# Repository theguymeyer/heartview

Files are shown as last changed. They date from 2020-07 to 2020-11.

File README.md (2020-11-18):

# Welcome to HeartView

A real-time testing system for pacemaker prototypes. 

The pacemaker project is a long standing challenge by Boston Scientific sponsored by McMaster University's Center for Software Certification -> [More](http://sqrl.mcmaster.ca/pacemaker.htm). This repo is the open-source (GPLv3) code base for the HeartView Testing GUI, embedded development files, and design files for the hardware and electrical systems. Even more info [here](https://guymeyer.me/project/heartview).

## Directory

HeartView Documentation -> https://github.com/theguymeyer/heartview/blob/master/course_dev/documentation/heartview_explained/intro_to_heartview.pdf

MacOS Executeable for HeartView -> https://github.com/theguymeyer/heartview/tree/master/course_dev/ui-HeartView/mac/exe

Windows Executeable for HeartView -> https://github.com/theguymeyer/heartview/tree/master/course_dev/ui-HeartView/win/exe

Nucleo Embedded Codebase -> https://github.com/theguymeyer/heartview/tree/master/course_dev/shield_nucleo_rev0/CubeMX

PCB Build Packages -> https://github.com/theguymeyer/heartview/tree/master/course_dev/Production/build

Heart Shield Design (Nucleo) -> https://github.com/theguymeyer/heartview/tree/master/course_dev/shield_nucleo_rev0

Pacemaker Shield Design -> https://github.com/theguymeyer/heartview/tree/master/course_dev/shield_pacemaker

Mechanical Design (casing) -> https://github.com/theguymeyer/heartview/tree/master/course_dev/casing/rev0

Testing Files -> https://github.com/theguymeyer/heartview/tree/master/course_dev/testing

## How to get involved

We invite you to contribute and help build a robust way to learn about pacemakers in a fun and engaging way. Reach out to the McSCert Research Group at McMaster Univeristy or get in touch view GitHub.

image of the heartview testing system The HeartView System

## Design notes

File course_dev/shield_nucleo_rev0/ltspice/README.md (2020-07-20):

# Documentation for the testing controller shield

The model is developed using LTspice with imported models. No model was found for the TLE2426CDR Rail Splitter chip so the model does not currently compile

The most up-to-date model is titled "nucleo_shield_heart_interface_rev2.asc"

### Notes on In Amp circuitry

- This Circuit was designed from information in this document (p.5-3 was especially helpful) (https://www.analog.com/media/en/training-seminars/design-handbooks/designers-guide-instrument-amps-complete.pdf)
- Desired Gain: 1/2
- Vcm = GND // the middle of the expected input dynamic range 
- note... the in-amp’s input buffers will need to swing both positive and negative with respect to ground
- Vref = 2.5V //  centered on the expected output dynamic range
- "A good guideline is to keep IBR < 10 mV" (p.5-3)
- Need to use "1% metal film resistors"

### Notes on pulse generation circuitry

Pulse Characteristics:
 - 5V square pulse
 - duration ranges from 100 us to 5 ms (according to PACEMAKER doc)

**IMPORTANT** The onboard toggle switch found on the pacemaker shield MUST be placed to 'x100' in order to comply with the pulse characteristics
 
Note: Recent discoveries in pacemaker shield show that the 
pulse is substantially filtered when nearing 3ms PW or below

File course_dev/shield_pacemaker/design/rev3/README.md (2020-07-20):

# Pacemaker Shield - Revision 3

Use this folder to store files related to the current revision developed by CG Tech Inc (Company Contact: Gil Elgez)

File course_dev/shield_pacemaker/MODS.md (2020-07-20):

# Shield Modifications

This document specifies the alterations needed for the Pacemaker shield (shield A). The current design of the shield can be found under,
        >> design >> rev2

## Mod 1 - Pin Swaps

The current revision (rev2) of the shield contains incorrect pin routing on certain pins. The corrections are outlined in "pin_swap_mod.png"

## Mod 2 - Replacing Connector X1

The goal is to provide a solution that will be allow for easy connections of jumper wires.
Note that each pin is connected twice to the board, a single PCB connection is **assumed** to suffice.

Instructions:
- update the BOM to include female header pins 
- ensure that the PCB matches the updated pins

## Mod 3 - Replacing Connector SV1

The current pins are incompatible with standard jumper wires. As such this part is to be changed in BOM to include 0.1" male header pins that fit female jumper wires connectors.

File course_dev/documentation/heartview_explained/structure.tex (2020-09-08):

%%%%%%%%%%%%%%%%%%%%%%%%%%%%%%%%%%%%%%%%%
% The Legrand Orange Book
% Structural Definitions File
% Version 2.1 (26/09/2018)
%
% Original author:
% Mathias Legrand (legrand.mathias@gmail.com) with modifications by:
% Vel (vel@latextemplates.com)
% 
% This file was downloaded from:
% http://www.LaTeXTemplates.com
%
% License:
% CC BY-NC-SA 3.0 (http://creativecommons.org/licenses/by-nc-sa/3.0/)
%
%%%%%%%%%%%%%%%%%%%%%%%%%%%%%%%%%%%%%%%%%

%----------------------------------------------------------------------------------------
%	VARIOUS REQUIRED PACKAGES AND CONFIGURATIONS
%----------------------------------------------------------------------------------------

\usepackage{graphicx} % Required for including pictures
\graphicspath{{res/}} % Specifies the directory where pictures are stored

\usepackage{lipsum} % Inserts dummy text

\usepackage{tikz} % Required for drawing custom shapes

\usepackage[english]{babel} % English language/hyphenation

\usepackage{enumitem} % Customize lists
\setlist{nolistsep} % Reduce spacing between bullet points and numbered lists

\usepackage{booktabs} % Required for nicer horizontal rules in tables

\usepackage{xcolor} % Required for specifying colors by name
\definecolor{ocre}{RGB}{243,102,25} % Define the orange color used for highlighting throughout the book

%----------------------------------------------------------------------------------------
%	MARGINS
%----------------------------------------------------------------------------------------

\usepackage{geometry} % Required for adjusting page dimensions and margins

\geometry{
	paper=a4paper, % Paper size, change to letterpaper for US letter size
	top=3cm, % Top margin
	bottom=3cm, % Bottom margin
	left=3cm, % Left margin
	right=3cm, % Right margin
	headheight=14pt, % Header height
	footskip=1.4cm, % Space from the bottom margin to the baseline of the footer
	headsep=10pt, % Space from the top margin to the baseline of the header
	%showframe, % Uncomment to show how the type block is set on the page
}

%----------------------------------------------------------------------------------------
%	FONTS
%----------------------------------------------------------------------------------------

\usepackage{avant} % Use the Avantgarde font for headings
%\usepackage{times} % Use the Times font for headings
\usepackage{mathptmx} % Use the Adobe Times Roman as the default text font together with math symbols from the Sym­bol, Chancery and Com­puter Modern fonts

\usepackage{microtype} % Slightly tweak font spacing for aesthetics
\usepackage[utf8]{inputenc} % Required for including letters with accents
\usepackage[T1]{fontenc} % Use 8-bit encoding that has 256 glyphs

%----------------------------------------------------------------------------------------
%	BIBLIOGRAPHY AND INDEX
%----------------------------------------------------------------------------------------

% original source code - broken for my installtion
%\usepackage[style=numeric,citestyle=numeric,sorting=nyt,sortcites=true,autopunct=true,babel=hyphen,hyperref=true,abbreviate=false,backref=true,backend=biber]{biblatex}
%\addbibresource{bibliography.bib} % BibTeX bibliography file
%\defbibheading{bibempty}{}

\usepackage[style=numeric, sorting=none, backend=bibtex, backref, doi=false]{biblatex}	% Use Biblatex for customization of bib
\addbibresource{./bibliography.bib} % BibTeX bibliography file

\usepackage{calc} % For simpler calculation - used for spacing the index letter headings correctly
\usepackage{makeidx} % Required to make an index
\makeindex % Tells LaTeX to create the files required for indexing

%----------------------------------------------------------------------------------------
%	MAIN TABLE OF CONTENTS
%----------------------------------------------------------------------------------------

\usepackage{titletoc} % Required for manipulating the table of contents

\contentsmargin{0cm} % Removes the default margin

% Part text styling (this is mostly taken care of in the PART HEADINGS section of this file)
\titlecontents{part}
	[0cm] % Left indentation
	{\addvspace{20pt}\bfseries} % Spacing and font options for parts
	{}
	{}
	{}

% Chapter text styling
\titlecontents{chapter}
	[1.25cm] % Left indentation
	{\addvspace{12pt}\large\sffamily\bfseries} % Spacing and font options for chapters
	{\color{ocre!60}\contentslabel[\Large\thecontentslabel]{1.25cm}\color{ocre}} % Formatting of numbered sections of this type
	{\color{ocre}} % Formatting of numberless sections of this type
	{\color{ocre!60}\normalsize\;\titlerule*[.5pc]{.}\;\thecontentspage} % Formatting of the filler to the right of the heading and the page number

% Section text styling
\titlecontents{section}
	[1.25cm] % Left indentation
	{\addvspace{3pt}\sffamily\bfseries} % Spacing and font options for sections
	{\contentslabel[\thecontentslabel]{1.25cm}} % Formatting of numbered sections of this type
	{} % Formatting of numberless sections of this type
	{\hfill\color{black}\thecontentspage} % Formatting of the filler to the right of the heading and the page number

% Subsection text styling
\titlecontents{subsection}
	[1.25cm] % Left indentation
	{\addvspace{1pt}\sffamily\small} % Spacing and font options for subsections
	{\contentslabel[\thecontentslabel]{1.25cm}} % Formatting of numbered sections of this type
	{} % Formatting of numberless sections of this type
	{\ \titlerule*[.5pc]{.}\;\thecontentspage} % Formatting of the filler to the right of the heading and the page number

% Figure text styling
\titlecontents{figure}
	[1.25cm] % Left indentation
	{\addvspace{1pt}\sffamily\small} % Spacing and font options for figures
	{\thecontentslabel\hspace*{1em}} % Formatting of numbered sections of this type
	{} % Formatting of numberless sections of this type
	{\ \titlerule*[.5pc]{.}\;\thecontentspage} % Formatting of the filler to the right of the heading and the page number

% Table text styling
\titlecontents{table}
	[1.25cm] % Left indentation
	{\addvspace{1pt}\sffamily\small} % Spacing and font options for tables
	{\thecontentslabel\hspace*{1em}} % Formatting of numbered sections of this type
	{} % Formatting of numberless sections of this type
	{\ \titlerule*[.5pc]{.}\;\thecontentspage} % Formatting of the filler to the right of the heading and the page number

%----------------------------------------------------------------------------------------
%	MINI TABLE OF CONTENTS IN PART HEADS
%----------------------------------------------------------------------------------------

% Chapter text styling
\titlecontents{lchapter}
	[0em] % Left indentation
	{\addvspace{15pt}\large\sffamily\bfseries} % Spacing and font options for chapters
	{\color{ocre}\contentslabel[\Large\thecontentslabel]{1.25cm}\color{ocre}} % Chapter number
	{}  
	{\color{ocre}\normalsize\sffamily\bfseries\;\titlerule*[.5pc]{.}\;\thecontentspage} % Page number

% Section text styling
\titlecontents{lsection}
	[0em] % Left indentation
	{\sffamily\small} % Spacing and font options for sections
	{\contentslabel[\thecontentslabel]{1.25cm}} % Section number
	{}
	{}

% Subsection text styling (note these aren't shown by default, display them by searchings this file for tocdepth and reading the commented text)
\titlecontents{lsubsection}
	[.5em] % Left indentation
	{\sffamily\footnotesize} % Spacing and font options for subsections
	{\contentslabel[\thecontentslabel]{1.25cm}}
	{}
	{}

%----------------------------------------------------------------------------------------
%	HEADERS AND FOOTERS
%----------------------------------------------------------------------------------------

\usepackage{fancyhdr} % Required for header and footer configuration

\pagestyle{fancy} % Enable the custom headers and footers

\renewcommand{\chaptermark}[1]{\markboth{\sffamily\normalsize\bfseries\chaptername\ \thechapter.\ #1}{}} % Styling for the current chapter in the header
\renewcommand{\sectionmark}[1]{\markright{\sffamily\normalsize\thesection\hspace{5pt}#1}{}} % Styling for the current section in the header

\fancyhf{} % Clear default headers and footers
\fancyhead[LE,RO]{\sffamily\normalsize\thepage} % Styling for the page number in the header
\fancyhead[LO]{\rightmark} % Print the nearest section name on the left side of odd pages
\fancyhead[RE]{\leftmark} % Print the current chapter name on the right side of even pages
%\fancyfoot[C]{\thepage} % Uncomment to include a footer

\renewcommand{\headrulewidth}{0.5pt} % Thickness of the rule under the header

\fancypagestyle{plain}{% Style for when a plain pagestyle is specified
	\fancyhead{}\renewcommand{\headrulewidth}{0pt}%
}

% Removes the header from odd empty pages at the end of chapters
\makeatletter
\renewcommand{\cleardoublepage}{
\clearpage\ifodd\c@page\else
\hbox{}
\vspace*{\fill}
\thispagestyle{empty}
%\newpage
\fi}

%----------------------------------------------------------------------------------------
%	THEOREM STYLES
%----------------------------------------------------------------------------------------

\usepackage{amsmath,amsfonts,amssymb,amsthm} % For math equations, theorems, symbols, etc

\newcommand{\intoo}[2]{\mathopen{]}#1\,;#2\mathclose{[}}
\newcommand{\ud}{\mathop{\mathrm{{}d}}\mathopen{}}
\newcommand{\intff}[2]{\mathopen{[}#1\,;#2\mathclose{]}}
\renewcommand{\qedsymbol}{$\blacksquare$}
\newtheorem{notation}{Notation}[chapter]

% Boxed/framed environments
\newtheoremstyle{ocrenumbox}% Theorem style name
{0pt}% Space above
{0pt}% Space below
{\normalfont}% Body font
{}% Indent amount
{\small\bf\sffamily\color{ocre}}% Theorem head font
{\;}% Punctuation after theorem head
{0.25em}% Space after theorem head
{\small\sffamily\color{ocre}\thmname{#1}\nobreakspace\thmnumber{\@ifnotempty{#1}{}\@upn{#2}}% Theorem text (e.g. Theorem 2.1)
\thmnote{\nobreakspace\the\thm@notefont\sffamily\bfseries\color{black}---\nobreakspace#3.}} % Optional theorem note

\newtheoremstyle{blacknumex}% Theorem style name
{5pt}% Space above
{5pt}% Space below
{\normalfont}% Body font
{} % Indent amount
{\small\bf\sffamily}% Theorem head font
{\;}% Punctuation after theorem head
{0.25em}% Space after theorem head
{\small\sffamily{\tiny\ensuremath{\blacksquare}}\nobreakspace\thmname{#1}\nobreakspace\thmnumber{\@ifnotempty{#1}{}\@upn{#2}}% Theorem text (e.g. Theorem 2.1)
\thmnote{\nobreakspace\the\thm@notefont\sffamily\bfseries---\nobreakspace#3.}}% Optional theorem note

\newtheoremstyle{blacknumbox} % Theorem style name
{0pt}% Space above
{0pt}% Space below
{\normalfont}% Body font
{}% Indent amount
{\small\bf\sffamily}% Theorem head font
{\;}% Punctuation after theorem head
{0.25em}% Space after theorem head
{\small\sffamily\thmname{#1}\nobreakspace\thmnumber{\@ifnotempty{#1}{}\@upn{#2}}% Theorem text (e.g. Theorem 2.1)
\thmnote{\nobreakspace\the\thm@notefont\sffamily\bfseries---\nobreakspace#3.}}% Optional theorem note

% Non-boxed/non-framed environments
\newtheoremstyle{ocrenum}% Theorem style name
{5pt}% Space above
{5pt}% Space below
{\normalfont}% Body font
{}% Indent amount
{\small\bf\sffamily\color{ocre}}% Theorem head font
{\;}% Punctuation after theorem head
{0.25em}% Space after theorem head
{\small\sffamily\color{ocre}\thmname{#1}\nobreakspace\thmnumber{\@ifnotempty{#1}{}\@upn{#2}}% Theorem text (e.g. Theorem 2.1)
\thmnote{\nobreakspace\the\thm@notefont\sffamily\bfseries\color{black}---\nobreakspace#3.}} % Optional theorem note
\makeatother

% Defines the theorem text style for each type of theorem to one of the three styles above
\newcounter{dummy} 
\numberwithin{dummy}{section}
\theoremstyle{ocrenumbox}
\newtheorem{theoremeT}[dummy]{Theorem}
\newtheorem{problem}{Problem}[chapter]
\newtheorem{exerciseT}{Exercise}[chapter]
\theoremstyle{blacknumex}
\newtheorem{exampleT}{Example}[chapter]
\theoremstyle{blacknumbox}
\newtheorem{vocabulary}{Vocabulary}[chapter]
\newtheorem{definitionT}{Definition}[section]
\newtheorem{corollaryT}[dummy]{Corollary}
\theoremstyle{ocrenum}
\newtheorem{proposition}[dummy]{Proposition}

%----------------------------------------------------------------------------------------
%	DEFINITION OF COLORED BOXES
%----------------------------------------------------------------------------------------

\RequirePackage[framemethod=default]{mdframed} % Required for creating the theorem, definition, exercise and corollary boxes

% Theorem box
\newmdenv[skipabove=7pt,
skipbelow=7pt,
backgroundcolor=black!5,
linecolor=ocre,
innerleftmargin=5pt,
innerrightmargin=5pt,
innertopmargin=5pt,
leftmargin=0cm,
rightmargin=0cm,
innerbottommargin=5pt]{tBox}

% Exercise box	  
\newmdenv[skipabove=7pt,
skipbelow=7pt,
rightline=false,
leftline=true,
topline=false,
bottomline=false,
backgroundcolor=ocre!10,
linecolor=ocre,
innerleftmargin=5pt,
innerrightmargin=5pt,
innertopmargin=5pt,
innerbottommargin=5pt,
leftmargin=0cm,
rightmargin=0cm,
linewidth=4pt]{eBox}	

% Definition box
\newmdenv[skipabove=7pt,
skipbelow=7pt,
rightline=false,
leftline=true,
topline=false,
bottomline=false,
linecolor=ocre,
innerleftmargin=5pt,
innerrightmargin=5pt,
innertopmargin=0pt,
leftmargin=0cm,
rightmargin=0cm,
linewidth=4pt,
innerbottommargin=0pt]{dBox}	

% Corollary box
\newmdenv[skipabove=7pt,
skipbelow=7pt,
rightline=false,
leftline=true,
topline=false,
bottomline=false,
linecolor=gray,
backgroundcolor=black!5,
innerleftmargin=5pt,
innerrightmargin=5pt,
innertopmargin=5pt,
leftmargin=0cm,
rightmargin=0cm,
linewidth=4pt,
innerbottommargin=5pt]{cBox}

% Creates an environment for each type of theorem and assigns it a theorem text style from the "Theorem Styles" section above and a colored box from above
\newenvironment{theorem}{\begin{tBox}\begin{theoremeT}}{\end{theoremeT}\end{tBox}}
\newenvironment{exercise}{\begin{eBox}\begin{exerciseT}}{\hfill{\color{ocre}\tiny\ensuremath{\blacksquare}}\end{exerciseT}\end{eBox}}				  
\newenvironment{definition}{\begin{dBox}\begin{definitionT}}{\end{definitionT}\end{dBox}}	
\newenvironment{example}{\begin{exampleT}}{\hfill{\tiny\ensuremath{\blacksquare}}\end{exampleT}}		
\newenvironment{corollary}{\begin{cBox}\begin{corollaryT}}{\end{corollaryT}\end{cBox}}	

%----------------------------------------------------------------------------------------
%	REMARK ENVIRONMENT
%----------------------------------------------------------------------------------------

\newenvironment{remark}{\par\vspace{10pt}\small % Vertical white space above the remark and smaller font size
\begin{list}{}{
\leftmargin=35pt % Indentation on the left
\rightmargin=25pt}\item\ignorespaces % Indentation on the right
\makebox[-2.5pt]{\begin{tikzpicture}[overlay]
\node[draw=ocre!60,line width=1pt,circle,fill=ocre!25,font=\sffamily\bfseries,inner sep=2pt,outer sep=0pt] at (-15pt,0pt){\textcolor{ocre}{R}};\end{tikzpicture}} % Orange R in a circle
\advance\baselineskip -1pt}{\end{list}\vskip5pt} % Tighter line spacing and white space after remark

%----------------------------------------------------------------------------------------
%	SECTION NUMBERING IN THE MARGIN
%----------------------------------------------------------------------------------------

\makeatletter
\renewcommand{\@seccntformat}[1]{\llap{\textcolor{ocre}{\csname the#1\endcsname}\hspace{1em}}}                    
\renewcommand{\section}{\@startsection{section}{1}{\z@}
{-4ex \@plus -1ex \@minus -.4ex}
{1ex \@plus.2ex }
{\normalfont\large\sffamily\bfseries}}
\renewcommand{\subsection}{\@startsection {subsection}{2}{\z@}
{-3ex \@plus -0.1ex \@minus -.4ex}
{0.5ex \@plus.2ex }
{\normalfont\sffamily\bfseries}}
\renewcommand{\subsubsection}{\@startsection {subsubsection}{3}{\z@}
{-2ex \@plus -0.1ex \@minus -.2ex}
{.2ex \@plus.2ex }
{\normalfont\small\sffamily\bfseries}}                        
\renewcommand\paragraph{\@startsection{paragraph}{4}{\z@}
{-2ex \@plus-.2ex \@minus .2ex}
{.1ex}
{\normalfont\small\sffamily\bfseries}}

%----------------------------------------------------------------------------------------
%	PART HEADINGS
%----------------------------------------------------------------------------------------

% Numbered part in the table of contents
\newcommand{\@mypartnumtocformat}[2]{%
	\setlength\fboxsep{0pt}%
	\noindent\colorbox{ocre!20}{\strut\parbox[c][.7cm]{\ecart}{\color{ocre!70}\Large\sffamily\bfseries\centering#1}}\hskip\esp\colorbox{ocre!40}{\strut\parbox[c][.7cm]{\linewidth-\ecart-\esp}{\Large\sffamily\centering#2}}%
}

% Unnumbered part in the table of contents
\newcommand{\@myparttocformat}[1]{%
	\setlength\fboxsep{0pt}%
	\noindent\colorbox{ocre!40}{\strut\parbox[c][.7cm]{\linewidth}{\Large\sffamily\centering#1}}%
}

\newlength\esp
\setlength\esp{4pt}
\newlength\ecart
\setlength\ecart{1.2cm-\esp}
\newcommand{\thepartimage}{}%
\newcommand{\partimage}[1]{\renewcommand{\thepartimage}{#1}}%
\def\@part[#1]#2{%
\ifnum \c@secnumdepth >-2\relax%
\refstepcounter{part}%
\addcontentsline{toc}{part}{\texorpdfstring{\protect\@mypartnumtocformat{\thepart}{#1}}{\partname~\thepart\ ---\ #1}}
\else%
\addcontentsline{toc}{part}{\texorpdfstring{\protect\@myparttocformat{#1}}{#1}}%
\fi%
\startcontents%
\markboth{}{}%
{\thispagestyle{empty}%
\begin{tikzpicture}[remember picture,overlay]%
\node at (current page.north west){\begin{tikzpicture}[remember picture,overlay]%	
\fill[ocre!20](0cm,0cm) rectangle (\paperwidth,-\paperheight);
\node[anchor=north] at (4cm,-3.25cm){\color{ocre!40}\fontsize{220}{100}\sffamily\bfseries\thepart}; 
\node[anchor=south east] at (\paperwidth-1cm,-\paperheight+1cm){\parbox[t][][t]{8.5cm}{
\printcontents{l}{0}{\setcounter{tocdepth}{1}}% The depth to which the Part mini table of contents displays headings; 0 for chapters only, 1 for chapters and sections and 2 for chapters, sections and subsections
}};
\node[anchor=north east] at (\paperwidth-1.5cm,-3.25cm){\parbox[t][][t]{15cm}{\strut\raggedleft\color{white}\fontsize{30}{30}\sffamily\bfseries#2}};
\end{tikzpicture}};
\end{tikzpicture}}%
\@endpart}
\def\@spart#1{%
\startcontents%
\phantomsection
{\thispagestyle{empty}%
\begin{tikzpicture}[remember picture,overlay]%
\node at (current page.north west){\begin{tikzpicture}[remember picture,overlay]%	
\fill[ocre!20](0cm,0cm) rectangle (\paperwidth,-\paperheight);
\node[anchor=north east] at (\paperwidth-1.5cm,-3.25cm){\parbox[t][][t]{15cm}{\strut\raggedleft\color{white}\fontsize{30}{30}\sffamily\bfseries#1}};
\end{tikzpicture}};
\end{tikzpicture}}
\addcontentsline{toc}{part}{\texorpdfstring{%
\setlength\fboxsep{0pt}%
\noindent\protect\colorbox{ocre!40}{\strut\protect\parbox[c][.7cm]{\linewidth}{\Large\sffamily\protect\centering #1\quad\mbox{}}}}{#1}}%
\@endpart}
\def\@endpart{\vfil\newpage
\if@twoside
\if@openright
\null
\thispagestyle{empty}%
%\newpage
\fi
\fi
\if@tempswa
\twocolumn
\fi}

%----------------------------------------------------------------------------------------
%	CHAPTER HEADINGS
%----------------------------------------------------------------------------------------

% A switch to conditionally include a picture, implemented by Christian Hupfer
\newif\ifusechapterimage
\usechapterimagetrue
\newcommand{\thechapterimage}{}%
\newcommand{\chapterimage}[1]{\ifusechapterimage\renewcommand{\thechapterimage}{#1}\fi}%
\newcommand{\autodot}{.}
\def\@makechapterhead#1{%
{\parindent \z@ \raggedright \normalfont
\ifnum \c@secnumdepth >\m@ne
\if@mainmatter
\begin{tikzpicture}[remember picture,overlay]
\node at (current page.north west)
{\begin{tikzpicture}[remember picture,overlay]
\node[anchor=north west,inner sep=0pt] at (0,0) {\ifusechapterimage\fi};
\draw[anchor=west] (\Gm@lmargin,-9cm) node [line width=2pt,rounded corners=15pt,draw=ocre,fill=white,fill opacity=0.5,inner sep=15pt]{\strut\makebox[22cm]{}};
\draw[anchor=west] (\Gm@lmargin+.3cm,-9cm) node {\huge\sffamily\bfseries\color{black}\thechapter\autodot~#1\strut};
\end{tikzpicture}};
\end{tikzpicture}
\else
\begin{tikzpicture}[remember picture,overlay]
\node at (current page.north west)
{\begin{tikzpicture}[remember picture,overlay]
\node[anchor=north west,inner sep=0pt] at (0,0) {\ifusechapterimage\fi};
\draw[anchor=west] (\Gm@lmargin,-9cm) node [line width=2pt,rounded corners=15pt,draw=ocre,fill=white,fill opacity=0.5,inner sep=15pt]{\strut\makebox[22cm]{}};
\draw[anchor=west] (\Gm@lmargin+.3cm,-9cm) node {\huge\sffamily\bfseries\color{black}#1\strut};
\end{tikzpicture}};
\end{tikzpicture}
\fi\fi\par\vspace*{270\p@}}}

%-------------------------------------------

\def\@makeschapterhead#1{%
\begin{tikzpicture}[remember picture,overlay]
\node at (current page.north west)
{\begin{tikzpicture}[remember picture,overlay]
\node[anchor=north west,inner sep=0pt] at (0,0) {\ifusechapterimage\fi};
\draw[anchor=west] (\Gm@lmargin,-9cm) node [line width=2pt,rounded corners=15pt,draw=ocre,fill=white,fill opacity=0.5,inner sep=15pt]{\strut\makebox[22cm]{}};
\draw[anchor=west] (\Gm@lmargin+.3cm,-9cm) node {\huge\sffamily\bfseries\color{black}#1\strut};
\end{tikzpicture}};
\end{tikzpicture}
\par\vspace*{270\p@}}
\makeatother

%----------------------------------------------------------------------------------------
%	LINKS
%----------------------------------------------------------------------------------------

\usepackage{hyperref}
\hypersetup{hidelinks,backref=true,pagebackref=true,hyperindex=true,colorlinks=false,breaklinks=true,urlcolor=ocre,bookmarks=true,bookmarksopen=false}

\usepackage{bookmark}
\bookmarksetup{
open,
numbered,
addtohook={%
\ifnum\bookmarkget{level}=0 % chapter
\bookmarksetup{bold}%
\fi
\ifnum\bookmarkget{level}=-1 % part
\bookmarksetup{color=ocre,bold}%
\fi
}
}

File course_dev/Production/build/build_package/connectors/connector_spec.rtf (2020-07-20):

These are the connectors we require:

1) Cable A - see attached image for example
- Connector: molex/0351550400 (https://www.digikey.ca/en/products/detail/molex/0351550400/2405538)
- Length: 7 inches (we use this for prototyping 3m/3801-04 (https://www.digikey.ca/en/products/detail/3m/3801-04/8257531))
- Crimp/Housing: molex/0008700056 (https://www.digikey.ca/en/products/detail/molex/0008700056/2421861) (as recommended by Molex)
- No Heat shrink required
- Routing (assuming that Pin1 is designated by MK1 according to this spec 351550400_sd.pdf (https://www.molex.com/pdm_docs/sd/351550400_sd.pdf))
Connector 1 pin 1 – 1 pin 1 colour red connector 2
Pin 2 – 2 pin 2 colour white
Pin 3 – 3 pin 3 colour white
Pin 4 – 4 pin 4 colour white

2) Cable B - see attached image for example
- Connector: molex/0513820400 (https://www.digikey.ca/en/products/detail/molex/0513820400/3262671)
- Length: 7 inches (we use this for prototyping 3m/3801-04 (https://www.digikey.ca/en/products/detail/3m/3801-04/8257531))
- Crimp/Housing: molex/0561349000 (https://www.digikey.ca/en/products/detail/molex/0561349000/2405592) (as recommended by Molex.. see Sheet No. 7 of this spec 561340000-AS-000.pdf (https://www.molex.com/pdm_docs/as/561340000-AS-000.pdf))
- No Heat shrink required
- Routing (assuming that Pin1 is designated by "1" according to Sheet No. 8 of this spec 561340000-AS-000.pdf (https://www.molex.com/pdm_docs/as/561340000-AS-000.pdf))
Connector 1 pin 1 – 1 pin 1 colour red connector 2
Pin 2 – 2 pin 2 colour white
Pin 3 – 3 pin 3 colour white
Pin 4 – 4 pin 4 colour white

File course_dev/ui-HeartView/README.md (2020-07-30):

# PyQt5 Testing Interface UI - HeartView

This UI is main interface of the remote testing station. Users can build test routines using the **Control Panel** and see the pacing information in using the **Real Time Plots**

## Components

### Control Panel

The user can uses this UI component to build test routines. The user can set pacing information with the available buttons and dispatch the test routine to the testing controller (MCU: nucleo-f446RE in this implementation). The data is transmitted to the testing controller via serial and is updated in real-time.

### Real Time Plots

The user can use this UI component to see the resulting waveforms they generated using their pacemaker, along with the testing routine currently running on the Testing Controller. The objective is to allow the user to compare waveforms and ensure that their operation is correct. As a result, timing is strict and must match the actual MCU operation with high accuracy. 

## Error Handling

No device connected upon serial start - upon boot the system will try to connect to the testing controller via serial. If the device is not found on the given port then the status bar will be updated

No serial device connected upon send - if the user tries to send a test routine when no device is connected then the serial.Exception is caught and the status bar is updated.

## Supporting Libraries

The following are a set of Python3 Libraries that enable the functionality in this application.

1. [PyQt5 5.15.0](https://pypi.org/project/PyQt5/)
... Frameworks for all UI elements, and serial communication
... ``pip3 install PyQt5``
2. [pyqtgraph](https://pyqtgraph.readthedocs.io/en/latest/index.html)
... Used to generate responsive real-time plots
... ``pip3 install pyqtgraph`` (source [here](https://pypi.org/project/pyqtgraph/))
3. [QtAwesome](https://pypi.org/project/QtAwesome/)
... Used for button and label icons
... ``pip3 install QtAwesome``
4. [fpdf](https://pypi.org/project/fpdf/)
... Used to generate printer-friendly PDF report
... ``pip3 install fpdf``
5. [numpy](https://pypi.org/project/numpy/)
... Mathematical computation
... ``pip3 install numpy``
6. Standard Python3 Libraries: sys, os

## Distribution

Yet to be registered, this app is intended to be licensed under the GPL. As such it is possible to distribute HeartView due to its dependencies on PyQt5 and [fbs](https://build-system.fman.io/) (build system).

Currently in development, the distribution bundler is PyInstaller.

According to the PyInstaller documentation the end users "do not need to have Python installed at all"[\[docs\]](https://readthedocs.org/projects/pyinstaller/downloads/pdf/latest/). Good to note! In addition the docs note that in order to generate executables for a different OS, a different version of Python, or a 32-bit/64-bit machine then PyInstaller must be run on that platform. The first distribution is for macOS Catalina 15.5.0

In order to create a distributable bundle for OSX follow these instructions...

Create a virtual environment using Python3.7.7 (I use pyenv). My virtual environment is called pyqt-venv-py3.7.7, therefore run, 

`pyenv activate pyqt-venv-py3.7.7`

Ensure that the correct libraries are installed using `pip3 freeze`. Key libraries are mentioned above in "Supporting Libraries". To generate a bundled package for OSX run the following: 

`python3 -m PyInstaller --onefile --windowed HeartView.spec`

.. and confirm if applicable (yes, yes)

### Generating app

A bundler script was created to automate the process of file generation, create_macOS_bundle.sh

Manual:

```
NAME
    create_macOS_bundle.sh

DESCRIPTION
    used to compile a HeartView distributable for MacOS. Log info is dumped into 'build.txt' file which is unique for every run.

    -t      Type of bundle
                -t1 => one file
                -t0 => one directory
    
    -c1     Clear dist and build dirs 
                -c1 => clear
    
    -s      Apply codesign with certificate. The user must input  their certificate common name as an argument (something like this.. "Apple Development: Your Name (AAAA1A1A1A)")

EXAMPLES
    The following is how to generate a one-file app for macOS

        ./create_macOS_bundle_py2app.sh -t1 -c1 

    The following is how to generate a one-file app for macOS with code signing

        ./create_macOS_bundle_py2app.sh -t1 -s="Apple Development: Your Name (AAAA1A1A1A)" -c1 
```

### Code Signing

What a nightmare... The major reason for this component is to ensure that HeartView is a recognized app and can be freely distributed to all users.

After PyInstaller compilation it is time to sign the app found in dist/HeartView.app

Use this command to sign the app:
`codesign -s "$CERTIFICATE_COMMON_NAME" -v dist/HeartView.app --deep`

The `--deep` flag is an important addition to ensure that all files are signed.

Useful documentation by Apple when starting Codesigning [here](https://developer.apple.com/library/archive/documentation/Security/Conceptual/CodeSigningGuide/Procedures/Procedures.html)

Useful documentation by PyInstaller when starting Codesigning [here](https://github.com/pyinstaller/pyinstaller/wiki/Recipe-OSX-Code-Signing)

I was having code signing errors and the instructions by honey9 in this [post](https://developer.apple.com/forums/thread/86161?login=true) really helped

### Deployment

When testing on other machines, namely macs, I ran into several early stage problems. 

1) Apps in Quaratine: Since from an unknown developer HeartView was quarantined by macOS Sierra Version 10.12.6. This [post](https://apple.stackexchange.com/questions/181026/lsopenurlswithrole-failed-with-error-10810-cant-open-install-os-x-yosemite) resolved the issue.

2) Error loading Python lib... dlopen... libintl.8.dylib

The issue here is no reverse compatability for MacOS applications. The answer was indicated [here](https://github.com/pyinstaller/pyinstaller/issues/3418). As explained, in order to create copy for High Sierra and back the app much be compiled on a very like Mavericks. 

A viable solution as noted by **abulka** is to create a Mavericks copy on VMware and install the python, pyinstaller and the source code. The app should be forward compatible to High Sierra.

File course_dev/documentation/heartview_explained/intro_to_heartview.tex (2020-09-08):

%%%%%%%%%%%%%%%%%%%%%%%%%%%%%%%%%%%%%%%%%
% The Legrand Orange Book
% LaTeX Template
% Version 2.4 (26/09/2018)
%
% SOURCE: https://www.latextemplates.com/template/the-legrand-orange-book
%
% This template was downloaded from:
% http://www.LaTeXTemplates.com
%
% Original author:
% Mathias Legrand (legrand.mathias@gmail.com) with modifications by:
% Vel (vel@latextemplates.com)
%
% License:
% CC BY-NC-SA 3.0 (http://creativecommons.org/licenses/by-nc-sa/3.0/)
%
% Compiling this template:
% This template uses biber for its bibliography and makeindex for its index.
% When you first open the template, compile it from the command line with the 
% commands below to make sure your LaTeX distribution is configured correctly:
%
% 1) pdflatex main
% 2) makeindex main.idx -s StyleInd.ist
% 3) biber main
% 4) pdflatex main x 2
%
% After this, when you wish to update the bibliography/index use the appropriate
% command above and make sure to compile with pdflatex several times 
% afterwards to propagate your changes to the document.
%
% This template also uses a number of packages which may need to be
% updated to the newest versions for the template to compile. It is strongly
% recommended you update your LaTeX distribution if you have any
% compilation errors.
%
% Important note:
% Chapter heading images should have a 2:1 width:height ratio,
% e.g. 920px width and 460px height.
%
%%%%%%%%%%%%%%%%%%%%%%%%%%%%%%%%%%%%%%%%%

%----------------------------------------------------------------------------------------
%	PACKAGES AND OTHER DOCUMENT CONFIGURATIONS
%----------------------------------------------------------------------------------------

\documentclass[11pt,fleqn]{book} % Default font size and left-justified equations

\input{structure.tex} % Insert the commands.tex file which contains the majority of the structure behind the template

%\hypersetup{pdftitle={Title},pdfauthor={Author}} % Uncomment and fill out to include PDF metadata for the author and title of the book

\usepackage[printonlyused,withpage]{acronym} 
\usepackage{xcolor}
\usepackage{pdflscape}

%----------------------------------------------------------------------------------------

\begin{document}

%----------------------------------------------------------------------------------------
%	TITLE PAGE
%----------------------------------------------------------------------------------------

\begingroup
\thispagestyle{empty} % Suppress headers and footers on the title page
\begin{tikzpicture}[remember picture,overlay]
\node[inner sep=0pt] (background) at (current page.center) {};
\draw (current page.center) node [fill=ocre!30!white,fill opacity=0.2,text opacity=1,inner sep=1cm]{\Huge\centering\bfseries\sffamily\parbox[c][][t]{\paperwidth}{\centering Intro to HeartView\\[15pt] % Book title
{\Large A Remote Testing Station for Pacemakers}\\[20pt] % Subtitle
{\huge Guy Meyer}}}; % Author name
\end{tikzpicture}
\vfill
\endgroup

%----------------------------------------------------------------------------------------
%	COPYRIGHT PAGE
%----------------------------------------------------------------------------------------

\newpage
~\vfill
\thispagestyle{empty}

\setlength\parindent{0pt}

\noindent GPLv3 Copyright \copyright\ 2020 Guy Meyer\\ % Copyright notice

\noindent \textsc{Published by Guy Meyer}\\ % Publisher

\noindent \textsc{github.com/theguymeyer/heartview}\\ % URL

\noindent Licensed under the GNU General Public License version 3 (GPLv3) (the ``License''). This License is a free, copyleft license for software and other kinds of works. You can review the terms of this License at \url{https://www.gnu.org/licenses/gpl-3.0.en.html}. \\ % License information, replace this with your own license (if any)

\noindent \textit{First printing, August 2020} % Printing/edition date

%----------------------------------------------------------------------------------------
%	TABLE OF CONTENTS
%----------------------------------------------------------------------------------------

%\usechapterimagefalse % If you don't want to include a chapter image, use this to toggle images off - it can be enabled later with \usechapterimagetrue

\chapterimage{chapter_head_1_pcb.pdf}\cite{piklist} % Table of contents heading image

\pagestyle{empty} % Disable headers and footers for the following pages

\tableofcontents % Print the table of contents itself

%\cleardoublepage % Forces the first chapter to start on an odd page so it's on the right side of the book

\pagestyle{fancy} % Enable headers and footers again

\newpage

\section*{List of Acronyms}
\addcontentsline{toc}{chapter}{List of Acronyms}
\begin{acronym}
	%Define acronyms here
	%Use intext with \ac{}. Look at reference for the acronym package for a full guide
	\acro{ADC}{analog to digital convertor}
	\acro{BPM}{Beats Per Minute}
	\acro{MCU}{microcontroller}
	\acro{PCB}{printed circuit board}
	\acro{OS}{operating system}
	\acro{UART}{universal asynchronous receiver-transmitter}

\end{acronym}

%----------------------------------------------------------------------------------------
%	PART
%----------------------------------------------------------------------------------------

%\part{Part One}

%----------------------------------------------------------------------------------------
%	CHAPTER 1
%----------------------------------------------------------------------------------------

\chapterimage{chapter_head_3_ecg.pdf}\cite{dr_med} % Chapter heading image

\chapter{Introduction}

\section{What is it?}\index{Description}

Learn about pacemakers! HeartView is an all-in-one remote testing system for designing pacemaker prototypes. Users can create models using their favourite development environment, deploy to the device, and test in a real-time environment. 

%------------------------------------------------

\section{The Pacemaker Challenge}\index{Pacemaker Challenge}

Boston Scientific has released into the public domain the system specification for a previous generation pacemaker. A major reason for publishing this specification is to have it serve as the basis for a challenge to the formal methods community, in the spirit of other Grand Challenges \cite{sqrl_pacemaker}.

%------------------------------------------------

\section{Motivation}\index{Motivation}

Over the last few years our group at McMaster University have converted this challenge into an integrated lab supporting a course on software development. The document supports the design process for the students and the development of the pacemaker is split into several assignments completed over the course of the semester. This hands-on learning style has shown success in recent years, seen through student engagement, attendance, and enrollment.\\

The evolution of this product jumped when schools closed due to the global pandemic sending students to learn online. The need for a remote method of development gave rise to HeartView, a remote testing system for pacemaker. Students can now study the mechanics of a pacemaker, and with the physiology of the heart anywhere they go.\\

%------------------------------------------------

%----------------------------------------------------------------------------------------
%	CHAPTER 2
%----------------------------------------------------------------------------------------

\chapter{The HeartView System}

\section{System Components}\index{System Components}

The HeartView testing environment is composed of three pillars software, electrical, and hardware. 

%------------------------------------------------

\subsection{Software}\index{System Components!Software}

The software used for this project can be broken down into two components; the tool used to control the physiology of the heart (used for testing), and that used to program the pacemaker.

%------------------------------------------------

\subsubsection{Heart}\index{System Components!Software!Heart}

The software used to control the heart is the HeartView UI. Meant to be installed on your local machine and communicate with the testing system via serial communication. The HeartView UI receives data from the heart, dispatches test routines, plots real-time data, and supports data analysis, as well as report generation.

%------------------------------------------------

\subsubsection{Pacemaker}\index{System Components!Software!Pacemaker}

In the first version of HeartView (used during the creation of this document), the \ac{MCU} used for the pacemaker is the FRDM K64F. Software can be written using Mbed Studio, MATLAB Simulink (used at McMaster), or other supported frameworks. The essence is to generate a binary file (.bin) that can be flashed (uploaded) onto the board. Learn more below in Section \ref{sec:prog_pacemaker}.

%------------------------------------------------

\subsection{Electrical}\index{System Components!Electrical}

In order to create a cardiac simulator two components have to work in parallel, the heart and the pacemaker. 

%------------------------------------------------

\subsubsection{Heart}\index{System Components!Electrical!Heart}

The \ac{MCU} used to power the heart heart is the Nucleo F446RE. It comes equipped with a \ac{PCB} shield that shares signals with the pacemaker via ribbon cables (mimicking the functionality of the electrodes). As an overview, the Nucleo collects electrical signals from the pacemaker using an AD8220 Instrumentation Amplifier and an onboard \ac{ADC}. Signals are sampled and sent to the HeartView UI for plotting via \ac{UART}, ie. serial communication.\\ 

The Nucleo is also responsible for generating natural heart signals according to the test routine constructed in the HeartView UI. Every time a new test routine is dispatched from HeartView, the test is parsed and implmented by the Nucleo in real-time. This is what provides the interactive experience of the HeartView Testing Station. The Nucleo shield also includes a pair of LEDs that pulse with every natural pace giving the user visual indication of natural heart activity.

%------------------------------------------------
\subsubsection{Pacemaker}\index{System Components!Electrical!Pacemaker}

The pacemaker is a FRDM K64F \ac{MCU} with a shield designed to mimic the electrical composition of a the real implantable device. More can be learned about the pacemaker shield in the ``Pacemaker Shield Explained" document.

%------------------------------------------------

\subsection{Hardware}\index{System Components!Hardware}

Though most of the complexity is in the software and electrical components, the hardware was not trivial. In essence, the hardware is meant to encase the test station and create a comfortable testing environment. Since it is unclear what space is available for the students, priority was given to creating a small form factor device that can protect the electronics without restricting access to key peripherals like the user buttons, and serial connectors. Laser cut covers were made for both sides to ensure that the students can study the electronics without the risk of damaging the device.\\

\begin{figure}[h]
	\centering
	\caption{HeartView testing station hardware}
	\label{fig:ts_overview} % Unique label used for referencing the figure in-text
	%\addcontentsline{toc}{figure}{Figure \ref{fig:placeholder}} % Uncomment to add the figure to the table of contents
\end{figure}

%------------------------------------------------

\section{Downloading the Software}\index{Downloading the Software}\label{sec:downloading_the_software}

Since HeartView is licensed under the GPLv3 Open Source License, the software is available for free on Github. Follow the link corresponding to your \ac{OS} where you can find a zip file that includes the bundled executable.

\subsection{Windows}\index{Installation!Windows}

Windows 10 >>\\ \url{https://github.com/theguymeyer/heartview/blob/master/course_dev/ui-HeartView/win/exe/heartview_win10.zip}

\subsection{MacOS}\index{Installation!MacOS}

MacOS 10.4 or newer >>\\ \url{https://github.com/theguymeyer/heartview/blob/master/course_dev/ui-HeartView/mac/exe/heartview_mac.zip}

\subsection{Linux (Debian/Ubuntu)}\index{Installation!Linux}

Not Supported (Coming Soon!)

%------------------------------------------------

\section{Setting It Up}\index{Setting It Up}

\subsection{Connecting to a Computer}

In order to connect to HeartView a single USB slot is required to connect the Heart (Nucleo board). Follow the instructions in Section \ref{sec:serialcontrols} to connect establish communication between the test station and the UI. Another USB slot is required to upload/flash programs to the pacemaker (FRDM board). If working in a group, you can plug the devices into different computers and interface using the test station. See Figure \ref{fig:system_plugin} to understand how to connect everything together.

\begin{figure}[h]
	\centering
	\label{fig:system_plugin} % Unique label used for referencing the figure in-text
	%\addcontentsline{toc}{figure}{Figure \ref{fig:placeholder}} % Uncomment to add the figure to the table of contents
\end{figure}

\subsection{Dispatching Your First Test}

To get started with the test station follow the following setups:\\

\begin{enumerate}
	\item Download the .zip (see Sec \ref{sec:downloading_the_software})
	\item Unzip
	\item Run the HeartView executeable (double click the icon)
		\begin{itemize}
			\item MacOS may list this app as an Unknown Developer. To overcome this right-click the icon and select ``Open" from the drop-down menu
		\end{itemize}
	\item Connect the 4 pin cables between the heart and pacemaker (as shown in Figure \ref{fig:ts_cables})
	\item Plug in the test station using both USB cables provided (See Figure \ref{fig:system_plugin} )
		\begin{itemize}
			\item \underline{FRDM K64F connects using a mini-USB}. Ensure that you are connected to the OpenSDA port (on right hand-side of the ethernet port when viewing from the top with the pacemaker on the left side of the testing station).
			\item \underline{Nucleo F446RE connects using a micro-USB}.
		\end{itemize}
	\item Press refresh button on the ``Serial Controls" options (found in the HeartView UI) to see the connected devices (see Figure \ref{fig:serial_controls})
	\item Find the correct serial ID for the Heart (nucleo)
		\begin{itemize}
			\item On MacOS would be similar to `cu.usbmodem144203'
			\item On Windows would be similar to `COM7'
		\end{itemize}
	\item Press connect (see Figure \ref{fig:serial_controls})
	\item Setup the characteristics you want
	\item Dispatch the test routine by pressing the ``Dispatch" button
\end{enumerate}

\begin{figure}[h]
	\centering
	\caption{HeartView testing station with connected cables}
	\label{fig:ts_cables} % Unique label used for referencing the figure in-text
	%\addcontentsline{toc}{figure}{Figure \ref{fig:placeholder}} % Uncomment to add the figure to the table of contents
\end{figure}

%------------------------------------------------

\section{Development and Testing}\index{Development and Testing}

\subsection{Programming a Pacemaker}\index{Development and Testing!Programming a Pacemaker}\label{sec:prog_pacemaker}

The pacemaker can be developed using your preferred environment where compatible binaries can be generated. At McMaster University, the MATLAB Simulink environment is used. The Simulink tool provides an easy-to-use interface with support for the FRDM K64F via the \href{https://www.mathworks.com/matlabcentral/fileexchange/55318-simulink-coder-support-package-for-nxp-frdm-k64f-board}{\textcolor{blue}{\underline{support package}}}.\\ 

Based on the pacing mode you'd like to develop, use the Simulink blocks, charts, and subsystems to model the correct functionality. The tool is also an effective way of abstracting the code and focusing of functional correctness. Once you are comfortable with the code and would like to begin real-time testing flash the board and use HeartView.\\

To learn about the pacemaker and to understand how to detect and generate pulses read the Pacemaker Shield Explained document. 

%------------------------------------------------

\subsection{Controlling the Heart}\index{Development and Testing!Controlling the Heart}

In this section we're going to dive into each components of the HeartView UI. It is important to remember that the UI is used to generate test conditions for the pacemaker, and can only control characteristics of the heart. See Section \ref{sec:prog_pacemaker} which outlines methods for developing the pacemaker.

As an overview refer to Figure \ref{fig:ui_overview} which outlines the different components of the HeartView UI. Let's go through them...

\subsubsection*{Signal Plots}
The core of HeartView is in the central signal plots that display atrial activity (upper plot), and ventricular activity (lower plot) in real-time. Each plot depicts both natural heart activity (red), and artificial pacemaker activity (blue). The plots indicate millivolt measurements in the vertical axis, and millisecond timing in the horizontal axis. Users can zoom in to a specific region by performing a click-hold and drag within the plot. 

\subsubsection*{Serial Controls} \label{sec:serialcontrols}
To collect real-time data, the computer running HeartView must be connected via USB to the Nucleo F446RE (the heart). Once plugged in, it can be selected from the drop-down menu found in the Serial Controls section. It is recommended to first plug in the Nucleo, select the correct serial port and then connect the pacemaker (if to the same computer), this will help identify the correct port. \\

In the case the the serial port does not show, press the blue reset button to the left of the drop-down menu. This will refresh the list and update any new devices plugged in. Once selected press ``Connect". 

\begin{figure}[h]
	\centering
	\caption{Serial controls options in HeartView UI}
	\label{fig:serial_controls} % Unique label used for referencing the figure in-text
	%\addcontentsline{toc}{figure}{Figure \ref{fig:placeholder}} % Uncomment to add the figure to the table of contents
\end{figure}

\subsubsection*{Test Case Builder} 
This is where the fun begins! A test case is made of four (4) components; Atrial Activity, Ventricular Activity, Heart Rate, and AV Delay. Use these controls to construct the desired operating conditions of the heart. This is primarily useful to perform functional testing for the pacemaker. In addition, chambers can be turned ON or OFF using the toggle buttons. \\

For example, operating mode AAI pacing at 60 \ac{BPM}  can be well tested by observing the pacemaker filling in the missing beats under these conditions... \\

\begin{itemize}
	\item Natural Atrium is turned ON
	\item Natural Ventricle is turned OFF
	\item Natural Atrial Pulse Width is set to 20 ms
	\item Natural Heart Rate is set to 30 BPM
	\item Natural AV Delay can be ignored 
\end{itemize}

Further verification can be achieved by slowly lowering the Atrial Pulse width until it is no longer detected. This tests the detection threshold of the pacemaker.

\subsubsection*{Dispatcher} 
Test routines are not active until they are dispatched using the ``Dispatch" button. This is to ensure that the user can focus on a specific test. 

\subsubsection*{Active Test Label} 
The information listed in this label describes the test routine currently loaded on into the heart. Users can be confident in their tests by ensuring that the correct test is dispatched and loaded. 

\subsubsection*{Help Page} 
If you forget the function HeartView, click this help button for quick refresher! 

\begin{figure}[h]
	\centering
	\caption{Help button to open tutorial on how to operate HeartView}
	\label{fig:button_help} % Unique label used for referencing the figure in-text
	%\addcontentsline{toc}{figure}{Figure \ref{fig:placeholder}} % Uncomment to add the figure to the table of contents
\end{figure}

\subsubsection*{Report Generation} 
described in Section \ref{sec:generating_report} 

\subsubsection*{Plotter Controls}
The plots upload data in real-time. Use these buttons to pause, start and reset data being displayed in the plots. Pausing the data does not stop the flow of new readings, as such, while paused all incoming data will be lost. When starting the plots from a stopped position, the plots will reset and data will begin plotting immediately, therefore, it is recommended to allow a few seconds before recording any data. Finally, resetting the plots simply performs an auto-range on the axes so that the data is seen correctly. 

\begin{figure}[h]
	\centering
	\centering
	\centering
	\caption{Controls for the HeartView Real-Time Plots (from left to right; stop, start, reset)}
	\label{fig:plotter_buttons} % Unique label used for referencing the figure in-text
	%\addcontentsline{toc}{figure}{Figure \ref{fig:placeholder}} % Uncomment to add the figure to the table of contents
\end{figure}

\begin{landscape}
\begin{figure}[h]
	\centering
	\caption{Component breakdown of the HeartView UI}
	\label{fig:ui_overview} % Unique label used for referencing the figure in-text
\end{figure}
\end{landscape}

%------------------------------------------------

\section{Generating Reports}\index{Generating Reports}\label{sec:generating_report}

Report generation is a useful tool for recording and distributing test results to others. Reports can be generated at any time by clicking the Printer button in the top right (see Figure \ref{fig:gen_report_icon}).

\begin{figure}[h]
	\centering
	\caption{Select this button to begin report generation}
	\label{fig:gen_report_icon} % Unique label used for referencing the figure in-text
	%\addcontentsline{toc}{figure}{Figure \ref{fig:placeholder}} % Uncomment to add the figure to the table of contents
\end{figure}

Once selected a menu will pop-up to build the report (see Figure \ref{fig:gen_report_menu}). Select/deselect the radio buttons to exclude specific sections, title the report with a personalized ID (note that a timestamp will be added after the report ID), and select a destination folder. Once the generation is complete then HeartView will display the file location underneath the graphs.\\ 

If the report is generated while HeartView is still outputting real-time data, then the report will include the data displayed when the ``Generate..." button is pressed. If you'd like specific data, then you should pause the graph prior to beginning report generation. 

\begin{figure}[h]
	\centering
	\caption{Select this button to begin report generation}
	\label{fig:gen_report_menu} % Unique label used for referencing the figure in-text
	%\addcontentsline{toc}{figure}{Figure \ref{fig:placeholder}} % Uncomment to add the figure to the table of contents
\end{figure}

\section{Troubleshooting}

\subsection{Unable to connect the Nucleo (Heart) in Windows}

You'll notice this issue when running HeartView, have connected the USB cable from the nucleo to your computer, but the nucleo board does not display in the serial drop-down menu.\\

First try to select the refresh button a couple of times after a minute to allow your machine time to detect the device. If you are still experiencing this issue where the port is undetected then your computer does not have the drivers installed. This can be fixed by following these steps:\\

\begin{enumerate}
	\item Disconnect the Nucleo from you computer
	\item Follow this link \href{https://www.st.com/en/development-tools/stsw-link009.html}{\textcolor{blue}{\underline{https://www.st.com/en/development-tools/stsw-link009.html}}}
	\begin{itemize}
		\item You may need to be a member to download the software
	\end{itemize}
	\item Select ``Get Software"
	\item Accept the License Agreement
	\item You will receive an email with a link to the same page
	\begin{itemize}
		\item Ensure that you are using the same browser session when accessing this link
	\end{itemize}
	\item Save the PDF and unzip..
	\item Follow the instruction in ``readme.txt"\\
\end{enumerate}

\underline{Note:} You can verify driver incompatibility by going to the ``Device Manager" and verifying that the Nucleo is only listed as a Portable Device and not under Ports. Once the driver is installer you will see it in the list of COM Ports.\\

Once the drivers are installed simply restart HeartView and connect to the correct COM Port.

%------------------------------------------------

%----------------------------------------------------------------------------------------
%	PART
%----------------------------------------------------------------------------------------

%\part{Part Two}

%----------------------------------------------------------------------------------------
%	CHAPTER 3
%----------------------------------------------------------------------------------------

\chapterimage{chapter_head_2_vangogh.pdf}\cite{van_gogh} % Chapter heading image

\chapter{Developer Notes}

\section{The Github Project}\index{github}

HeartView is a copy-left, open-source project. In essence, it is an introductory tool to learn about pacemakers. To view the source code or the hardware design visit the original Github project (https://github.com/theguymeyer/heartview). In the repo you can also find useful information about design and development, along with the original source code. \\

To become a contributor just reach out!

\section{HeartView UI - readme}\index{developer_heartview}

The HeartView UI is the main interface of the remote testing station. Users can build test routines using the \textbf{Control Panel} and see the pacing information in using the \textbf{Real Time Plots}.

\subsection{Components}

\subsubsection{Control Panel}

The user can uses this UI component to build test routines. The user can set pacing information with the available buttons and dispatch the test routine to the testing controller (MCU: nucleo-f446RE in this implementation). The data is transmitted to the testing controller via serial and is updated in real-time.

\subsubsection{Real Time Plots}

The user can use this UI component to see the resulting waveforms they generated using their pacemaker, along with the testing routine currently running on the Testing Controller. The objective is to allow the user to compare waveforms and ensure that their operation is correct. As a result, timing is strict and must match the actual MCU operation with high accuracy. 

\subsection{Error Handling}

No device connected upon serial start - upon boot the system will try to connect to the testing controller via serial. If the device is not found on the given port then the status bar will be updated.\\

No serial device connected upon send - if the user tries to send a test routine when no device is connected then the serial.Exception is caught and the status bar is updated.

\subsection{Supporting Libraries}

The following are a set of Python3 Libraries that enable the functionality in this application.

\begin{enumerate}
	\item \href{https://pypi.org/project/PyQt5/}{\textcolor{blue}{\underline{PyQt5 5.15.0}}}
	\begin{itemize}
		\item Frameworks for all UI elements, and serial communication
		\item \begin{verbatim}pip3 install PyQt5 \end{verbatim}
	\end{itemize}
	\item \href{https://pyqtgraph.readthedocs.io/en/latest/index.html}{\textcolor{blue}{\underline{pyqtgraph}}}
		\begin{itemize}
		\item Used to generate responsive real-time plots
		\item \begin{verbatim}pip3 install pyqtgraph \end{verbatim} (source \href{https://pypi.org/project/pyqtgraph/}{\textcolor{blue}{\underline{https://pypi.org/project/pyqtgraph/}}})
	\end{itemize}
	\item \href{https://pypi.org/project/QtAwesome/}{\textcolor{blue}{\underline{QtAwesome}}}
		\begin{itemize}
		\item Used for button and label icons
		\item \begin{verbatim}pip3 install QtAwesome \end{verbatim}
	\end{itemize}
	\item \href{https://pypi.org/project/fpdf/}{\textcolor{blue}{\underline{fpdf}}}
		\begin{itemize}
		\item Used to generate printer-friendly PDF report
		\item \begin{verbatim}pip3 install fpdf \end{verbatim}
	\end{itemize}
	\item \href{https://pypi.org/project/numpy/}{\textcolor{blue}{\underline{numpy}}}
		\begin{itemize}
			\item Mathematical computation
			\item \begin{verbatim}pip3 install numpy \end{verbatim}
		\end{itemize}
	\item Standard Python3 Libraries: sys, os
\end{enumerate}

\subsection{Distribution}

This app is intended to be licensed under the GPLv3. As such it is possible to distribute HeartView due to its dependencies on PyQt5 and PyInstaller (bundling framework).\\

Currently in development, the distribution bundler is PyInstaller.\\

According to the PyInstaller documentation the end users ``do not need to have Python installed at all" \href{https://readthedocs.org/projects/pyinstaller/downloads/pdf/latest/}{\textcolor{blue}{\underline{docs}}}. Good to note! In addition the docs note that in order to generate executables for a different OS, a different version of Python, or a 32-bit/64-bit machine then PyInstaller must be run on that platform. The first distribution is for macOS Catalina 15.5.0.\\

In order to create a distributable bundle for OSX follow these instructions...\\

Create a virtual environment using Python3.7.7 (I use pyenv). My virtual environment is called pyqt-venv-py3.7.7, therefore run, \\

\begin{verbatim}pyenv activate pyqt-venv-py3.7.7 \end{verbatim}

Ensure that the correct libraries are installed using `pip3 freeze`. Key libraries are mentioned above in "Supporting Libraries". To generate a bundled package for OSX run the following: 

\begin{verbatim}python3 -m PyInstaller --onefile --windowed HeartView.spec \end{verbatim}

.. and confirm if applicable (yes, yes)\\

\textbf{INFO PLIST}\\

The info.plist file is a distribution file manadatory for OSx applications. The purpose of this file is to outline the bundle specification of the app. PyInstaller includes the info.plist file along with the bundle.

\subsubsection{Generating app}

A bundler script was created to automate the process of file generation, \textit{create\_macOS\_bundle.sh}. Windows bundling follows similar rules, a batch file is included in the Github repo to aid in bundling Windows exe's.\\

\underline{Manual:}

\begin{verbatim}
NAME 
create\_macOS\_bundle.sh

DESCRIPTION
used to compile a HeartView distributable for MacOS. 
Log info is dumped into 'build.txt' file which is unique for every run.

-t      Type of bundle
-t1 => one file
-t0 => one directory

-c1     Clear dist and build dirs 
-c1 => clear

-s      Apply codesign with certificate. 
The user must input  their certificate common name as an argument 
(Like this.. "Apple Development: Your Name (AAAA1A1A1A)")

EXAMPLES
The following is how to generate a one-file app for macOS

./create\_macOS\_bundle.sh -t1 -c1 

The following is how to generate a one-file app for macOS with code signing

./create\_macOS\_bundle.sh -t1 -s="Apple Development: Your Name (AAAA1A1A1A)" -c1 
\end{verbatim}

\subsubsection{Code Signing}

The major reason for this component is to ensure that HeartView is a recognized app and can be freely distributed to all users.\\

After PyInstaller compilation it is time to sign the app found in dist/HeartView.app

Use this command to sign the app:\\
\begin{verbatim}codesign -s "\$CERTIFICATE\_COMMON\_NAME" -v dist/HeartView.app --deep \end{verbatim}

The ``--deep" flag is an important addition to ensure that all files are signed.\\

Useful documentation by Apple when starting Codesigning \href{https://developer.apple.com/library/archive/documentation/Security/Conceptual/CodeSigningGuide/Procedures/Procedures.html}{\textcolor{blue}{\underline{here}}}\\

Useful documentation by PyInstaller when starting Codesigning \href{https://github.com/pyinstaller/pyinstaller/wiki/Recipe-OSX-Code-Signing}{\textcolor{blue}{\underline{here}}}\\

I was having code signing errors and the instructions by honey9 in this \href{https://developer.apple.com/forums/thread/86161?login=true}{\textcolor{blue}{\underline{post}}} really helped

\subsection{Deployment}

When testing on other machines, namely macs, I ran into several early stage problems. \\

\begin{enumerate}
	\item Apps in Quaratine: Since from an unknown developer HeartView was quarantined by macOS Sierra Version 10.12.6. This \href{https://apple.stackexchange.com/questions/181026/lsopenurlswithrole-failed-with-error-10810-cant-open-install-os-x-yosemite}{\textcolor{blue}{\underline{post}}} resolved the issue.
	
	\item LSOpenURL... (-10810) - occurs when an app that is not codesigning is downloaded to a MacOS system. Ensure that signatures have been applied and that the Bundle and Executable are named the same.
\end{enumerate}

The issue here is no reverse compatability for MacOS applications. The answer was indicated \href{https://github.com/pyinstaller/pyinstaller/issues/3418}{\textcolor{blue}{\underline{here}}}. As explained, in order to create copy for High Sierra and back the app much be compiled on a very like Mavericks. \\

A viable solution as noted by \textbf{abulka} is to create a Mavericks copy on VMware and install the python, PyInstaller and the source code. The app should be forward compatible to High Sierra.

\section{Development Issues}

\subsection{Electrical}

A notable electrical issue was found when functional testing began. The issue is with the I/O system of the heart which filters the incoming DC signal from the pacemaker. The instrumentation amplifier used is the AD8220 which performs common-mode rejection on between the inputs. As a result the pacemaker signal is not displayed accurately in HeartView. Assuming a correct implementation in Simulink, the pacemaker will output a signal similar to that depicted in Figure \ref{fig:signal_pacemaker} - left, but due to the errors in circuit design then the signal appears as shown in Figure \ref{fig:signal_pacemaker} - right.

\begin{figure}[h]
	\centering
	\centering
	\caption{Signal output by pacemaker (left), signal shown in HeartView (right)}
	\label{fig:signal_pacemaker} % Unique label used for referencing the figure in-text
	%\addcontentsline{toc}{figure}{Figure \ref{fig:placeholder}} % Uncomment to add the figure to the table of contents
\end{figure}

\cleardoublepage

%------------------------------------------------

%----------------------------------------------------------------------------------------
%	BIBLIOGRAPHY
%----------------------------------------------------------------------------------------

% but why???? the printbib command is before the chapter start but the pdf renders fine...... ugh latex!
\printbibliography
\chapter*{Bibliography}
\addcontentsline{toc}{chapter}{\textcolor{ocre}{Bibliography}} % Add a Bibliography heading to the table of contents

%----------------------------------------------------------------------------------------
%	INDEX
%----------------------------------------------------------------------------------------

%\cleardoublepage % Make sure the index starts on an odd (right side) page
%\phantomsection
%\setlength{\columnsep}{0.75cm} % Space between the 2 columns of the index
%\addcontentsline{toc}{chapter}{\textcolor{ocre}{Index}} % Add an Index heading to the table of contents
%\printindex % Output the index

%----------------------------------------------------------------------------------------

\begin{figure}[h]
	\centering
	\label{fig:fireball} % Unique label used for referencing the figure in-text
	%\addcontentsline{toc}{figure}{Figure \ref{fig:placeholder}} % Uncomment to add the figure to the table of contents
\end{figure}

\centering
Sponsored by McMaster University Department of Computing and Software

\end{document}

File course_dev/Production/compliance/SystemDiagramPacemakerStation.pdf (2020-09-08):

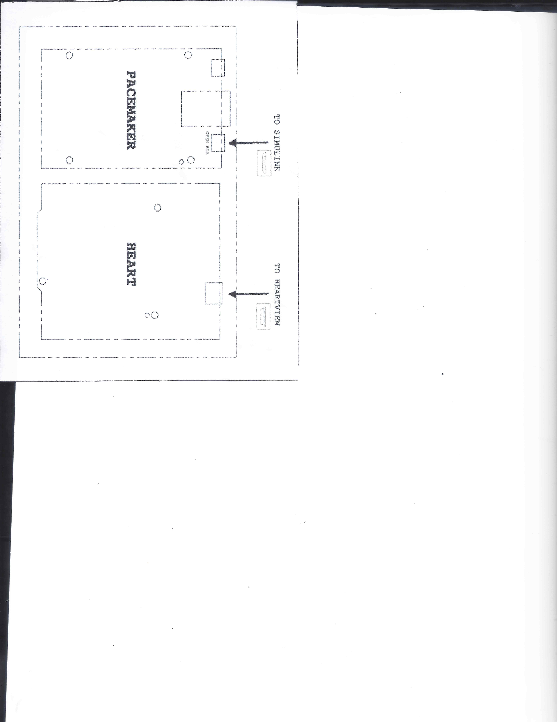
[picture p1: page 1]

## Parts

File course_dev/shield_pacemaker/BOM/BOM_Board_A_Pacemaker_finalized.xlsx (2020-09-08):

BOM - Board A (Pacemaker)
# | Designator | Quantity | Comment | Value | Footprint | Description | Manufacturer | Price | Total Price
1 | C32 | 1 | CAP CER 0.022UF 50V X7R 0805 | C0805C223K5RACTU | 0805 | SMD/SMT 50V 0.022uF X7R 0805 10% | KEMET | $0.15 | $0.15
2 | C31 | 1 | CAP CER 0.039UF 50V X7R 0805 | C0805C393K5RACTU | 0805 | SMD/SMT 50V 0.039uF X7R 0805 10% | KEMET | $0.34 | $0.34
3 | C1, C3, C6, C14, C17, C27, C29, C30, C33, C39, C41, C43, C46, C48 | 14 | CAP CER 0.1UF 50V X7R 0805 | C0805C104J5RACTU | 0805 | SMD/SMT 50V 0.1uF X7R 0805 5% | KEMET | $0.20 | $2.73
4 | C35 | 1 | CAP CER 0.22UF 16V X7R 0805 | C0805C224K4RACTU | 0805 | SMD/SMT 16V 0.22uF X7R 0805 10% | KEMET | $0.30 | $0.30
5 | C34 | 1 | CAP CER 0.39UF 50V X7R 0805 | C0805X394K5RACTU | 0805 | SMD/SMT 50V 0.39uF X7R 0805 10% | KEMET | $0.98 | $0.98
6 | R19, R20 | 2 | RES SMD 1.02K OHM 1% 1/8W 0805 | ERJ-6ENF1021V | 0805 | SMD 0805 1.02Kohms 1% | Panasonic Electronic Components | $0.16 | $0.32
7 | R25, R26 | 2 | RES SMD 1.4M OHM 1% 1/8W 0805 | ERJ-6ENF1404V | 0805 | SMD 0805 1.4Mohms 1% | Panasonic Electronic Components | $0.16 | $0.32
8 | C23, C24, C25, C26 | 4 | CAP CER 1.5UF 50V X7R 0805 | C2012X7R1H155K125AC | 0805 | SMD/SMT 0805 50V 1.5uF X7R 10% | TDK Corporation | $1.09 | $4.36
9 | R7, R9 | 2 | RES SMD 100K OHM 1% 1/8W 0805 | ERJ-6ENF1003V | 0805 | SMD 0805 100Kohms 1% | Panasonic Electronic Components | $0.16 | $0.32
10 | R49, R50 | 2 | RES SMD 10M OHM 1% 1/8W 0805 | CRCW080510M0FKEB | 0805 | SMD 1/8watt 10Mohms 1% | Vishay Dale | $0.16 | $0.32
11 | R13, R14, R15, R16, R39, R40, R42, R45, R46, R47, R48, R51, R52 | 13 | RES SMD 10K OHM 1% 1/8W 0805 | ERJ-6ENF1002V | 0805 | SMD 0805 10Kohms 1% | Panasonic Electronic Components | $0.11 | $1.48
12 | C10, C11, C12, C13, C18, C19, C21, C22 | 8 | CAP CER 10UF 10V X5R 0805 | CL21A106KPFNNWE | 0805 | SMD/SMT 10V 10uF X7R 0805 10% | Samsung Electro-Mechanics | $0.27 | $2.16
13 | R33, R34 | 2 | RES SMD 133K OHM 1% 1/8W 0805 | ERJ-6ENF1333V | 0805 | SMD 0805 133Kohms 1% | Panasonic Electronic Components | $0.16 | $0.32
14 | R5, R6 | 2 | RES SMD 1M OHM 1% 1/8W 0805 | ERJ-6ENF1004V | 0805 | SMD 0805 1Mohms 1% Tol | Panasonic Electronic Components | $0.16 | $0.32
15 | R8, R10 | 2 | RES SMD 1K OHM 1% 1/8W 0805 | ERJ-6ENF1001V | 0805 | SMD 0805 1Kohms 1% | Panasonic Electronic Components | $0.16 | $0.32
16 | C2, C4, C5, C7, C8, C9, C15, C16, C20, C28, C36, C37, C38, C40, C42, C44, C45, C47 | 18 | CAP CER 1UF 16V X5R 0805 | C0805C105K4PACTU | 0805 | SMD/SMT 16V 1uF X5R 0805 10% | KEMET | $0.23 | $4.16
17 | R30 | 1 | RES SMD 22.1K OHM 1% 1/8W 0805 | ERJ-6ENF2212V | 0805 | SMD 0805 22.1Kohms 1% | Panasonic Electronic Components | $0.16 | $0.16
18 | R17, R18, R21, R22 | 4 | RES SMD 249K OHM 1% 1/8W 0805 | ERJ-6ENF2493V | 0805 | SMD 0805 249Kohms 1% | Panasonic Electronic Components | $0.16 | $0.64
19 | R12, R41 | 2 | RES SMD 3.3K OHM 1% 1/8W 0805 | ERJ-6ENF3301V | 0805 | SMD 0805 3.3Kohms 1% | Panasonic Electronic Components | $0.16 | $0.32
20 | R23, R24 | 2 | RES SMD 330K OHM 1% 1/8W 0805 | ERJ-6ENF3303V | 0805 | SMD 0805 330Kohms 1% | Panasonic Electronic Components | $0.16 | $0.32
21 | R29 | 1 | RES SMD 39K OHM 1% 1/8W 0805 | ERJ-6ENF3902V | 0805 | SMD 0805 39Kohms 1% | Panasonic Electronic Components | $0.16 | $0.16
22 | R35, R36, R37, R38, R43, R44 | 6 | RES SMD 4.99K OHM 1% 1/8W 0805 | ERJ-6ENF4991V | 0805 | SMD 0805 4.99Kohms 1% | Panasonic Electronic Components | $0.16 | $0.96
23 | R11 | 1 | RES SMD 5.49K OHM 1% 1/8W 0805 | ERJ-6ENF5491V | 0805 | SMD 0805 5.49Kohms 1% | Panasonic Electronic Components | $0.16 | $0.16
24 | R53, R54 | 2 | RES SMD 510K OHM 1% 1/8W 0805 | ERJ-6ENF5103V | 0805 | SMD 0805 510Kohms 1% | Panasonic Electronic Components | $0.16 | $0.32
25 | R1, R2, R3, R4, R55 | 5 | RES SMD 59 OHM 1% 1/8W 0805 | ERJ-6ENF59R0V | 0805 | SMD 0805 59.0ohms 1% Tol | Panasonic Electronic Components | $0.16 | $0.80
26 | R31, R32 | 2 | RES SMD 7.5K OHM 1% 1/8W 0805 | ERJ-6ENF7501V | 0805 | SMD 0805 7.5Kohms 1% | Panasonic Electronic Components | $0.16 | $0.32
27 | R27, R28 | 2 | RES SMD 715K OHM 1% 1/8W 0805 | ERJ-6ENF7153V | 0805 | SMD 0805 715Kohms 1% | Panasonic Electronic Components | $0.16 | $0.32
28 | D3, D4, D6, D7 | 4 | DIODE ARRAY SCHOTTKY 30V SOT23 | BAT54S,215 | SOT-23-3 | SCHOTTKY 30V DUAL | Nexperia USA Inc. | $0.21 | $0.84
29 | D5 | 1 | DIODE ZENER 3.3V 225MW SOT23-3 | BZX84C3V3LT1G | SOT-23-3 | DIODE ZENER 3.3V 225MW SOT23-3 | ON Semiconductor | $0.19 | $0.19
30 | U1, U7, U8, U9 | 4 | IC SWITCH QUAD 1X2 14TSSOP | CD74HC4066PWR | TSSOP-14 | IC SWITCH QUAD 1X2 14TSSOP | Texas Instruments | $0.86 | $3.44
31 | SW1 | 1 | SWITCH SLIDE 4PDT 200MA 30V | EG4208 |  | SWITCH SLIDE 4PDT 200MA 30V | E-Switch | $1.95 | $1.95
32 | U4, U5, U6 | 3 | IC OPAMP GP 4 CIRCUIT 14TSSOP | LMV774MT/NOPB | TSSOP-14 | IC OPAMP GP 4 CIRCUIT 14TSSOP | Texas Instruments | $4.45 | $13.35
33 | U10 | 1 | IC COMP 1.6V DUAL O-D 8SOIC | MCP6547-E/SN | SOIC-8 | IC COMP 1.6V DUAL O-D 8SOIC | Microchip Technology | $0.91 | $0.91
34 | U3 | 1 | IC VREF GND REF 20V 1% 8SOIC | TLE2426CDR | SOIC-8 | IC VREF GND REF 20V 1% 8SOIC | Texas Instruments | $3.29 | $3.29
35 | PACEOUT | 1 | 55932-0430 | 55932-0430 | B4B-PH-K-S | CONN HEADER VERT 4POS 2MM | Molex | $0.31 | $0.31
36 | HRTIN | 1 | 35312-0460 | 35312-0460 | B4B-XH-A | CONN HEADER VERT 4POS 2.5MM | Molex | $0.36 | $0.36
37 | J2 | 1 | PREC010SFAN-RC | PREC010SFAN-RC |  | CONN HEADER VERT 10POS 2.54MM | Sullins Connector Solutions | $0.26 | $0.26
38 | J3, J4 | 2 | PREC008SFAN-RC | PREC008SFAN-RC |  | CONN HEADER VERT 8POS 2.54MM | Sullins Connector Solutions | $0.21 | $0.41
39 | J1 | 1 | PREC006SFAN-RC | PREC006SFAN-RC |  | CONN HEADER VERT 6POS 2.54MM | Sullins Connector Solutions | $0.15 | $0.15
40 | IC1, IC2 | 2 | IC INST AMP 1 CIRCUIT 8SOIC | AD8226ARZ-R7 | 8SOIC | IC INST AMP 1 CIRCUIT 8SOIC | Analog Devices Inc. | $4.80 | $9.60
41 | JP1 | 0 | Test Point |  |  |  |  | $0.00 | $0.00
42 | JP2 | 0 | Test Point |  |  |  |  | $0.00 | $0.00
43 | JP3 | 0 | Test Point |  |  |  |  | $0.00 | $0.00
44 | JP4 | 0 | Test Point |  |  |  |  | $0.00 | $0.00
45 | JP5 | 0 | Test Point |  |  |  |  | $0.00 | $0.00
46 | A_IA_TP | 0 | Test Point |  |  |  |  | $0.00 | $0.00
47 | V_IA_TP | 0 | Test Point |  |  |  |  | $0.00 | $0.00
 |  |  |  |  |  |  |  | Total Price | $53.31

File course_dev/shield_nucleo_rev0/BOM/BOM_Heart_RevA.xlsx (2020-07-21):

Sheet: Part List Report
 | Component list |  | Bill of Materials for Variant [Production] of Project [Heart RevA.PrjPcb] (No PCB Document Selected)
 | Source Data From: |  | Heart RevA.PrjPcb
 | Project: |  | Heart RevA.PrjPcb
 | Variant: |  | Production
 | Report Date: | 2020-07-13 | 9:58 PM
 | Print Date: | 2020-07-20 | 44032.75656
# | Designator | Quantity | Comment | Value | Footprint | Description | Manufacturer | Price | Total Price
1 | C1, C5, C7, C10, C12, C15 | 6 | 0.1uF | CL10B104KB8NNNL | 0603_N_1MM | CAP CER 0.1UF 50V X7R 0603 | Samsung | 0.01 | 0.06
2 | C2, C6, C8, C11, C13, C16, C17 | 7 | 1uF | CL10B105KQ8NNNC | 0603_N | CAP CER 1UF 6.3V X7R 0603 | Samsung | 0.01 | 0.07
3 | C3, C4, C9, C14 | 4 | 3300pF | 885012006016 | 0603_N | CAP CER 3300PF 10V C0G/NP0 0603 | Würth Elektronik | 0.01 | 0.04
4 | HEART IN | 1 | 559320430 | 559320430 | B4B-PH-K-S | CONN HEADER VERT 4POS 2MM | Molex | 0.47 | 0.47
5 | HEART OUT | 1 | 353120460 | 353120460 | B4B-XH-A | CONN HEADER VERT 4POS 2.5MM | Molex | 0.16 | 0.16
6 | J1 | 1 | PREC006SFAN-RC | PREC006SFAN-RC |  | CONN HEADER VERT 6POS 2.54MM | Sullins Connector Solutions | 0.15 | 0.15
7 | J2 | 1 | PREC010SFAN-RC | PREC010SFAN-RC |  | CONN HEADER VERT 10POS 2.54MM | Sullins Connector Solutions | 0.26 | 0.26
8 | J3, J4 | 2 | PREC008SFAN-RC | PREC008SFAN-RC |  | CONN HEADER VERT 8POS 2.54MM | Sullins Connector Solutions | 0.21 | 0.41
9 | LED3 | 1 | TLHB44K2M1 | OVLBB4C7 | LED_5mm | LED BLUE CLEAR 3MM T/H | TT Electronics/Optek Technology | 0.51 | 0.51
10 | LED4 | 1 | 151051RS11000 | OVLBR4C7 | LED_5mm | LED RED CLEAR 3MM T/H | TT Electronics/Optek Technology | 0.51 | 0.51
11 | R1, R7 | 2 | 75K | RC0603FR-0775KL | 0603_N_RES | RES SMD 75K OHM 1% 1/10W 0603 | Yageo | 0.01 | 0.02
12 | R2, R6, R8, R12 | 4 | 162K | RC0603FR-07162KL | 0603_N_RES | RES SMD 162K OHM 1% 1/10W 0603 | Yageo | 0.01 | 0.04
13 | R3, R9, R17, R18 | 4 | 1K | RC0603FR-071KL | 0603_N_RES | RES SMD 1K OHM 1% 1/10W 0603 | Yageo | 0.01 | 0.04
14 | R4, R5, R10, R11, R19, R20 | 6 | 49.9K | RC0603FR-0749K9L | 0603_N_RES | RES SMD 49.9K OHM 1% 1/10W 0603 | Yageo | 0.01 | 0.06
15 | R13 | 1 | 100 | RC0603FR-07100RL | 0603_N_RES | RES SMD 100 OHM 1% 1/10W 0603 | Yageo | 0.01 | 0.01
16 | R14 | 1 | 150 | RC0603FR-07150RL | 0603_N_RES | RES SMD 150 OHM 1% 1/10W 0603 | Yageo | 0.01 | 0.01
17 | R15, R16 | 2 | 100K | RC0603FR-07100KL | 0603_N_RES | RES SMD 100K OHM 1% 1/10W 0603 | Yageo | 0.01 | 0.02
18 | U1, U3 | 2 | AD8220 | AD8220ARMZ-R7 | MSOP8_0.65mm_DGK | IC INST AMP 1 CIRCUIT 8MSOP | Analog Devices Inc. | 6.64 | 13.28
19 | U2 | 1 | TLE2426CDR | TLE2426CDR | SOIC8_SMTC | IC VREF GND REF 2.0V 1% 8SOIC | Texas Instruments | 2.23 | 2.23
Approved |  |  | Notes |  |  |  |  |  | $18.36

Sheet: Project Information
Project Full Path | C:\MyWork\Active_Projects\mcmaster\Board B\RevA\Heart RevA.PrjPcb
Project Filename | Heart RevA.PrjPcb
Variant Name | Production
Data-Source Filename | Heart RevA.PrjPcb
Data-Source Full Path | C:\MyWork\Active_Projects\mcmaster\Board B\RevA\Heart RevA.PrjPcb
Title | Bill of Materials for Variant [Production] of Project [Heart RevA.PrjPcb] (No PCB Document Selected)
Total Quantity | 48
Report Time | 9:58 PM
Report Date | 2020-07-13
Report Date & Tine | 2020-07-13 9:58 PM
Output Name | Bill of Materials
Output Type | BOM_PartType
Output Generator Name | BOM
Output Generator Description | Bill of Materials

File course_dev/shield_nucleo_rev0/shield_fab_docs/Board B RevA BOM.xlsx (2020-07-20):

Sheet: Export Summary
This document was exported from Numbers. Each table was converted to an Excel worksheet. All other objects on each Numbers sheet were placed on separate worksheets. Please be aware that formula calculations may differ in Excel.
Numbers Sheet Name | Numbers Table Name | Excel Worksheet Name
Part List Report
 | Table 1 | Part List Report
Project Information
 | Table 1 | Project Information

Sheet: Part List Report
 | Component list |  | Bill of Materials for PCB Document [Board B RevA.PcbDoc]
 | Source Data From: |  | Board B RevA.PcbDoc
 | Project: |  | Board B RevA.PrjPcb
 | Variant: |  | None
 | Report Date: | 26-Jun-20 | 5:52 PM
 | Print Date: | 2020-06-29 | 44011.74421
# | Designator | Quantity | Comment | Value | Footprint | Description | Manufacturer | Price | Total Price
1 | C1, C5, C7, C10, C12, C15 | 6 | 0.1uF | 06035C104KAT4A | 0603_N_1MM | CAP CER 0.1UF 50V X7R 0603 | AVX | 0.01 | 0.06
2 | C2, C6, C8, C11, C13, C16, C17 | 7 | 1uF | CL10B105KQ8NNNC | 0603_N | CAP CER 1UF 6.3V X7R 0603 | Samsung | 0.01 | 0.07
3 | C3, C4, C9, C14 | 4 | 3300pF | 885012006016 | 0603_N | CAP CER 3300PF 10V C0G/NP0 0603 | Würth Elektronik | 0.01 | 0.04
4 | HEART IN | 1 | B4B-PH-K-S | 55932-0430 | B4B-PH-K-S | CONN HEADER VERT 4POS 2MM | Molex | 0.14 | 0.14
5 | HEART OUT | 1 | B4B-XH-A | 35312-0460 | B4B-XH-A | CONN HEADER VERT 4POS 2.5MM | Molex | 0.14 | 0.14
6 | J1 | 1 | LHS-06-TS | 22-28-4065 | LHS-00-TS_OUTLINE | CONN HEADER VERT 6 POS 2.54MM | Molex | 1.65 | 1.65
7 | J2 | 1 | LHS-10-TS | 22-28-4102 | LHS-10-TS_OUTLINE | CONN HEADER VERT 10POS 2.54MM | Molex | 0.31 | 0.31
8 | J3, J4 | 2 | LHS-08-TS | 22-28-0080 | LHS-08-TS_OUTLINE | Header, 8-Pin | Molex | 1.65 | 3.30
9 | LED1 | 1 | VLMB1300-GS08 | VLMB1300-GS08 | LED_0603 | LED BLUE HIGHBRIGHT 0603 SMD | Vishay | 0.09 | 0.09
10 | LED2 | 1 | SML-D12V1WT86 | SML-D12V1WT86 | LED_0603 | Red LED 2.2V 0603 | Rohm Semiconductor | 0.10 | 0.10
11 | LED3 | 1 | 151051BS04000 | 151051BS04000 | LED_5mm | LED BLUE DIFFUSED 5MM ROUND T/H | Würth Elektronik | 0.29 | 0.29
12 | LED4 | 1 | 151051RS11000 | 151051RS11000 | LED_5mm | LED RED DIFFUSED 5MM ROUND T/H | Würth Elektronik | 0.19 | 0.19
13 | R1, R7 | 2 | 75K | RC0603FR-0775KL | 0603_N_RES | RES SMD 75K OHM 1% 1/10W 0603 | Yageo | 0.01 | 0.02
14 | R2, R6, R8, R12 | 4 | 162K | RC0603FR-07162KL | 0603_N_RES | RES SMD 162K OHM 1% 1/10W 0603 | Yageo | 0.01 | 0.04
15 | R3, R9, R17, R18 | 4 | 1K | RC0603FR-071KL | 0603_N_RES | RES SMD 1K OHM 1% 1/10W 0603 | Yageo | 0.01 | 0.04
16 | R4, R5, R10, R11, R19, R20 | 6 | 49.9K | RC0603FR-0749K9L | 0603_N_RES | RES SMD 49.9K OHM 1% 1/10W 0603 | Yageo | 0.01 | 0.06
17 | R13 | 1 | 100 | RC0603FR-07100RL | 0603_N_RES | RES SMD 100 OHM 1% 1/10W 0603 | Yageo | 0.01 | 0.01
18 | R14 | 1 | 150 | RC0603FR-07150RL | 0603_N_RES | RES SMD 150 OHM 1% 1/10W 0603 | Yageo | 0.01 | 0.01
19 | R15, R16 | 2 | 100K | RC0603FR-07100KL | 0603_N_RES | RES SMD 100K OHM 1% 1/10W 0603 | Yageo | 0.01 | 0.02
20 | U1, U3 | 2 | AD8220 | AD8220ARMZ-R7 | MSOP8_0.65mm_DGK | IC INST AMP 1 CIRCUIT 8MSOP | Analog Devices Inc. | 6.64 | 13.28
21 | U2 | 1 | TLE2426CDR | TLE2426CDR | SOIC8_SMTC | IC VREF GND REF 2.0V 1% 8SOIC | Texas Instruments | 2.23 | 2.23
22 | U4 | 1 | ARDUINO_R3 | n/a | ARDUINOR3 | Arduino R3 Shield | n/a | 0.00 | 0.00
Approved |  |  | Notes |  |  |  |  |  | $22.09

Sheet: Project Information
Project Full Path | C:\MyWork\Active_Projects\mcmaster\Board B\RevA\Board B RevA.PrjPcb
Project Filename | Board B RevA.PrjPcb
Variant Name | None
Data-Source Filename | Board B RevA.PcbDoc
Data-Source Full Path | C:\MyWork\Active_Projects\mcmaster\Board B\RevA\Board B RevA.PcbDoc
Title | Bill of Materials for PCB Document [Board B RevA.PcbDoc]
Total Quantity | 51
Report Time | 5:52 PM
Report Date | 26-Jun-20
Report Date & Tine | 26-Jun-20 5:52 PM
Output Name | Bill of Materials
Output Type | BOM_PartType
Output Generator Name | BOM
Output Generator Description | Bill of Materials

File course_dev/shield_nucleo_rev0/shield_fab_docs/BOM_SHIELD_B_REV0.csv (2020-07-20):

Manufacturer Part Number | Manufacturer | Digi-Key Part Number | Customer Reference | Reference Designator | Packaging | Part Status | Quantity | Unit Price | Extended Price | Quantity Available | Mfg Std Lead Time | Description | RoHS Status | Lead Free Status | REACH Status
AD8220ARMZ-R7 | Analog Devices Inc. | AD8220ARMZ-R7CT-ND | U1, U2 |  | Cut Tape (CT) | Active | 2 | 10.21000 | $20.42 | 4563 | 26 Weeks | IC INST AMP 1 CIRCUIT 8MSOP | ROHS3 Compliant | Lead free | REACH Unaffected
TLE2426CDR | Texas Instruments | 296-26774-1-ND | U3 |  | Cut Tape (CT) | Active | 1 | 3.29000 | $3.29 | 3640 | 6 Weeks | IC VREF GND REF 20V 1% 8SOIC | ROHS3 Compliant | Lead free | REACH Unaffected
ERJ-PA3F1001V | Panasonic Electronic Components | P1.0KBYCT-ND | R1,R2,R15,R16 |  | Cut Tape (CT) | Active | 4 | 0.22000 | $0.88 | 54868 | 12 Weeks | RES SMD 1K OHM 1% 1/4W 0603 | ROHS3 Compliant | Lead free | REACH Unaffected
ERJ-PA3F1623V | Panasonic Electronic Components | ERJ-PA3F1623V-ND | R3,R5,R7,R8,R9,R10 |  | Tape & Reel (TR) | Active | 6 | 0.00000 | $0.00 | 0 | 12 Weeks | RES SMD 162K OHM 1% 1/4W 0603 | ROHS3 Compliant | Lead free | REACH Unaffected
ERJ-PA3F4992V | Panasonic Electronic Components | ERJ-PA3F4992V-ND | R4,R6,R13,R14 |  | Tape & Reel (TR) | Active | 4 | 0.00000 | $0.00 | 0 | 12 Weeks | RES SMD 49.9K OHM 1% 1/4W 0603 | ROHS3 Compliant | Lead free | REACH Unaffected
ERJ-PA3F1002V | Panasonic Electronic Components | P10KBYCT-ND | R11,R12 |  | Cut Tape (CT) | Active | 2 | 0.22000 | $0.44 | 96712 | 12 Weeks | RES SMD 10K OHM 1% 1/4W 0603 | ROHS3 Compliant | Lead free | REACH Unaffected
ERJ-PA3F2200V | Panasonic Electronic Components | P220BYCT-ND | R17,R18 |  | Cut Tape (CT) | Active | 2 | 0.22000 | $0.44 | 7712 | 12 Weeks | RES SMD 220 OHM 1% 1/4W 0603 | ROHS3 Compliant | Lead free | REACH Unaffected
ERJ-PA3F1003V | Panasonic Electronic Components | P100KBYCT-ND | R19,R20 |  | Cut Tape (CT) | Active | 2 | 0.22000 | $0.44 | 55805 | 12 Weeks | RES SMD 100K OHM 1% 1/4W 0603 | ROHS3 Compliant | Lead free | REACH Unaffected
C0603C332K4RACTU | KEMET | 399-9065-1-ND | C5,C6,C7,C8 |  | Cut Tape (CT) | Active | 4 | 0.43000 | $1.72 | 6633 | 8 Weeks | CAP CER 3300PF 16V X7R 0603 | ROHS3 Compliant | Lead free | REACH Unaffected
C0603C105K4RACTU | KEMET | 399-7847-1-ND | C1,C3,C11,C12,C14,C15,C17 |  | Cut Tape (CT) | Active | 7 | 0.18000 | $1.26 | 620854 | 23 Weeks | CAP CER 1UF 16V X7R 0603 | ROHS3 Compliant | Lead free | REACH Unaffected
C0603C104K4RACTU | KEMET | 399-1096-1-ND | C2,C4,C9,C10,C13,C16 |  | Cut Tape (CT) | Active | 6 | 0.18000 | $1.08 | 1767574 | 8 Weeks | CAP CER 0.1UF 16V X7R 0603 | ROHS3 Compliant | Lead free | REACH Unaffected
IN-S126ATR | Inolux | 1830-1092-1-ND | D1 |  | Cut Tape (CT) | Active | 1 | 0.51000 | $0.51 | 3066 | 5 Weeks | LED RED CLEAR 1206 SMD | ROHS3 Compliant | Lead free | Not Available
IN-S126ATB | Inolux | 1830-1088-1-ND | D2 |  | Cut Tape (CT) | Active | 1 | 0.69000 | $0.69 | 1925 | 5 Weeks | LED BLUE CLEAR 1206 SMD | ROHS3 Compliant | Lead free | Not Available
B4B-XH-A(LF)(SN) | JST Sales America Inc. | 455-2249-ND | J1 |  | Bulk | Active | 1 | 0.31000 | $0.31 | 71099 | 16 Weeks | CONN HEADER VERT 4POS 2.5MM | ROHS3 Compliant | Lead free | REACH Unaffected
B4B-PH-K-S(LF)(SN) | JST Sales America Inc. | 455-1706-ND | J2 |  | Bulk | Active | 1 | 0.36000 | $0.36 | 0 | 16 Weeks | CONN HEADER VERT 4POS 2MM | RoHS Compliant | Lead free | Not Available
LHS-10-TS | Adam Tech | 2057-LHS-10-TS-ND | JA1 |  | Bag | Active | 1 | 0.55000 | $0.55 | 837 | 9 Weeks | CONN HEADER VERT 10POS 2.54MM | ROHS3 Compliant | Lead free | Not Available
LHS-08-TS | Adam Tech | 2057-LHS-08-TS-ND | JA2,JA3 |  | Bag | Active | 2 | 0.45000 | $0.90 | 1455 | 9 Weeks | CONN HEADER VERT 8POS 2.54MM | ROHS3 Compliant | Lead free | Not Available
LHS-06-TS | Adam Tech | 2057-LHS-06-TS-ND | JA4 |  | Bag | Active | 1 | 5.19000 | $5.19 | 100 | 9 Weeks | CONN HEADER VERT 6POS 2.54MM | ROHS3 Compliant | Lead free | Not Available
NUCLEO-F446RE | STMicroelectronics | 497-15882-ND | Dev board |  | Box | Active | 1 | 22.22000 | $22.22 | 0 | Not Available | NUCLEO-64 STM32F446RE DEV EVAL | ROHS3 Compliant | Lead free | REACH Unaffected

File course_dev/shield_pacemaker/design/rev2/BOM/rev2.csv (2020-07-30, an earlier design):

Qty | Value | Device | Package | Parts | Description | MF | MPN | OC_FARNELL | OC_NEWARK | PACKAGE | SUPPLIER | TP_SIGNAL_NAME
5 |  | PINHD-1X1 | 1X01 | JP1, JP2, JP3, JP4, JP5 | PIN HEADER
1 | 0.022uF | C-USC0805 | C0805 | C32 | CAPACITOR, American symbol
1 | 0.039uF | C-USC0805 | C0805 | C31 | CAPACITOR, American symbol
14 | 0.1uF | C-USC0805 | C0805 | C1, C3, C6, C14, C17, C27, C29, C30, C33, C39, C41, C43, C46, C48 | CAPACITOR, American symbol
1 | 0.22uF | C-USC0805 | C0805 | C35 | CAPACITOR, American symbol
1 | 0.39uF | C-USC0805 | C0805 | C34 | CAPACITOR, American symbol
2 | 1.02k | R-US_R0805 | R0805 | R19, R20 | RESISTOR, American symbol
2 | 1.4M | R-US_R0805 | R0805 | R25, R26 | RESISTOR, American symbol
4 | 1.5uF | C-USC0805 | C0805 | C23, C24, C25, C26 | CAPACITOR, American symbol
2 | 100k | R-US_R0805 | R0805 | R7, R9 | RESISTOR, American symbol
2 | 10M | R-US_R0805 | R0805 | R49, R50 | RESISTOR, American symbol
13 | 10k | R-US_R0805 | R0805 | R13, R14, R15, R16, R39, R40, R42, R45, R46, R47, R48, R51, R52 | RESISTOR, American symbol
8 | 10uF | C-USC0805 | C0805 | C10, C11, C12, C13, C18, C19, C21, C22 | CAPACITOR, American symbol
2 | 133k | R-US_R0805 | R0805 | R33, R34 | RESISTOR, American symbol
2 | 1M | R-US_R0805 | R0805 | R5, R6 | RESISTOR, American symbol
2 | 1k | R-US_R0805 | R0805 | R8, R10 | RESISTOR, American symbol
18 | 1uF | C-USC0805 | C0805 | C2, C4, C5, C7, C8, C9, C15, C16, C20, C28, C36, C37, C38, C40, C42, C44, C45, C47 | CAPACITOR, American symbol
1 | 22.1k | R-US_R0805 | R0805 | R30 | RESISTOR, American symbol
4 | 249k | R-US_R0805 | R0805 | R17, R18, R21, R22 | RESISTOR, American symbol
2 | 3.3k | R-US_R0805 | R0805 | R12, R41 | RESISTOR, American symbol
2 | 330k | R-US_R0805 | R0805 | R23, R24 | RESISTOR, American symbol
1 | 39k | R-US_R0805 | R0805 | R29 | RESISTOR, American symbol
6 | 4.99k | R-US_R0805 | R0805 | R35, R36, R37, R38, R43, R44 | RESISTOR, American symbol
1 | 5.49k | R-US_R0805 | R0805 | R11 | RESISTOR, American symbol
2 | 510k | R-US_R0805 | R0805 | R53, R54 | RESISTOR, American symbol
5 | 59 | R-US_R0805 | R0805 | R1, R2, R3, R4, R55 | RESISTOR, American symbol
2 | 7.5k | R-US_R0805 | R0805 | R31, R32 | RESISTOR, American symbol
2 | 715k | R-US_R0805 | R0805 | R27, R28 | RESISTOR, American symbol
2 | AD623R | AD623R | SO8 | IC1, IC2 | Single-Supply, Rail-to-Rail, Low Cost Instrumentation Amplifier |  | AD623ARZ. | 9426213 | 31M4186
1 | ARDUINOR3-DIMENSION | ARDUINOR3-DIMENSION | ARDUINOR3 | U2 | This is a new object for the new Arduino R3 - with extra pins that you may want to use (such as IOref, and duplicated A4/A5
4 | BAT54S | BAT54S | SOT23 | D3, D4, D6, D7 | Schottky Diodes
1 | BZX84C3V3LT1G | ZENER-DIODESOT23 | SOT23 | D5 | Z-Diode
4 | CD74HC4066PWR | CD74HC4066PWR | SOP65P640X110-14N | U1, U7, U8, U9
1 | ED7004-ND | MA04-1 | MA04-1 | SV1 | PIN HEADER |  |  | unknown | unknown
1 | EG4208 | EG4208 | EG4208-PACKAGE | SW1
6 | FIDUCIAL | FIDUCIAL | FIDUCIAL_1MM | U$1, U$2, U$3, U$4, U$5, U$6 | For use by pick and place machines to calibrate the vision/machine, 1mm
3 | LMV344MT | LMV344MT | SOP65P640X110-14N | U4, U5, U6
1 | MCP6547-E/SN | MCP6547-E/SN | SOIC127P600X175-8N | U10 | Open-Drain Output Sub-Microamp Comparators |  | MCP6547-E/SN | - | 71J5347 | SOIC-8 | Microchip
1 | TLE2426CDR | TLE2426CDR | SOIC127P600X175-8N | U3 | Precision Virtual Ground |  | TLE2426CDR | 1575632 | 76C7712 | SOIC-8 | Texas Instruments
2 | TPSTP06R | TPSTP06R | TP06R | A_IA_TP, V_IA_TP | TEST PIN
1 | TSW-104-02-S-Q | TSW-104-02-S-Q | TSW-104-02-S-Q | X1 | THROUGH-HOLE .025 SQ POST HEADER" |  |  | unknown | unknown

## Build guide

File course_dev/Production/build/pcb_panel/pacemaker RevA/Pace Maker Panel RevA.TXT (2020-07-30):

M48
;Layer_Color=9474304
;FILE_FORMAT=2:4
INCH,LZ
;TYPE=PLATED
T1F00S00C0.0120
T2F00S00C0.0130
T3F00S00C0.0150
T4F00S00C0.0160
T5F00S00C0.0300
T6F00S00C0.0315
T7F00S00C0.0394
T8F00S00C0.0400
T9F00S00C0.0420
T10F00S00C0.0472
%
T01
X00575Y00841
X005742Y00968
Y01248
X008312Y01234
X00965Y012485
Y00956
X00702Y0074
X01167Y006789
X00767Y013005
X00418Y01302
T02
X035806Y007045
X034821Y008502
X035724Y010577
X036278Y010825
X033483Y010785
T03
X00258Y01161
X00257Y012626
X006267Y011971
X010221Y011964
X00815Y013705
X00418Y013616
X00115Y01389
X01257Y01617
Y017059
X04186Y016108
X0423Y015198
X04617Y015268
X04186Y019288
T04
X047025Y010436
X0474Y010248
X04785
X048207Y010628
X048169Y012834
X0474Y012248
X0464
X0465Y012648
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

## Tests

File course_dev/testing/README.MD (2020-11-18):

# 1. Install Drivers & Tools
## Windows
    - ST-Link Driver: https://www.st.com/en/development-tools/stsw-link009.html 
## Linux
    - udev rules for stm32 board
## Windows, Linux, macOS
    - JLink Software Pack https://www.segger.com/downloads/jlink#J-LinkSoftwareAndDocumentationPack

# 2. Replace the bootloader on the K64F
    - Download JLink firmware for k64f https://www.segger.com/downloads/jlink/OpenSDA_FRDM-K64F
    - Hold the reset button while connecting the board to you computer
    - A bootloader drive/volume should show up
    - Copy the .bin file to the bootloader drive

# 3. Install Python dependencies (Python 3)
```sh
    pip3 install pipenv
    pipenv install
    pipenv run pyocd pack -i stm32f446re
```

# 4. Run the tests
```sh
    pipenv run python ./main.py
```

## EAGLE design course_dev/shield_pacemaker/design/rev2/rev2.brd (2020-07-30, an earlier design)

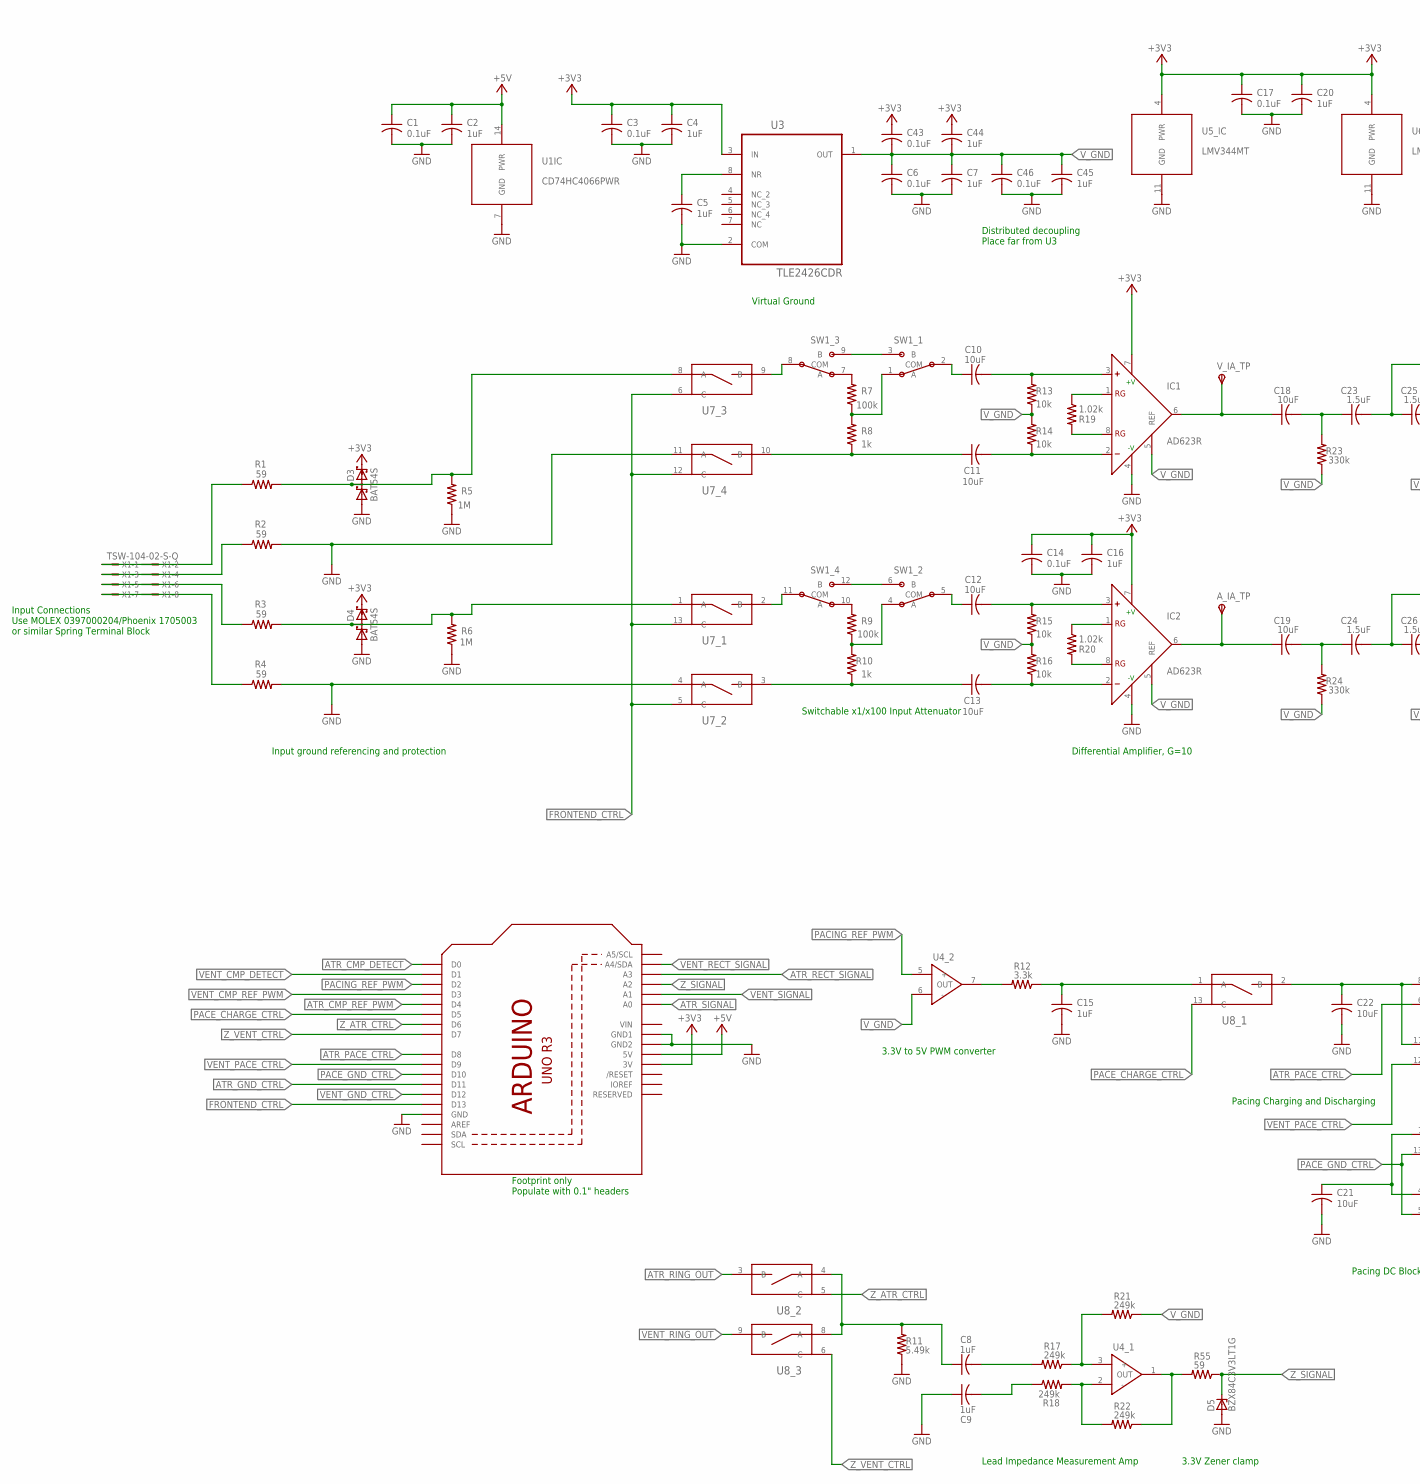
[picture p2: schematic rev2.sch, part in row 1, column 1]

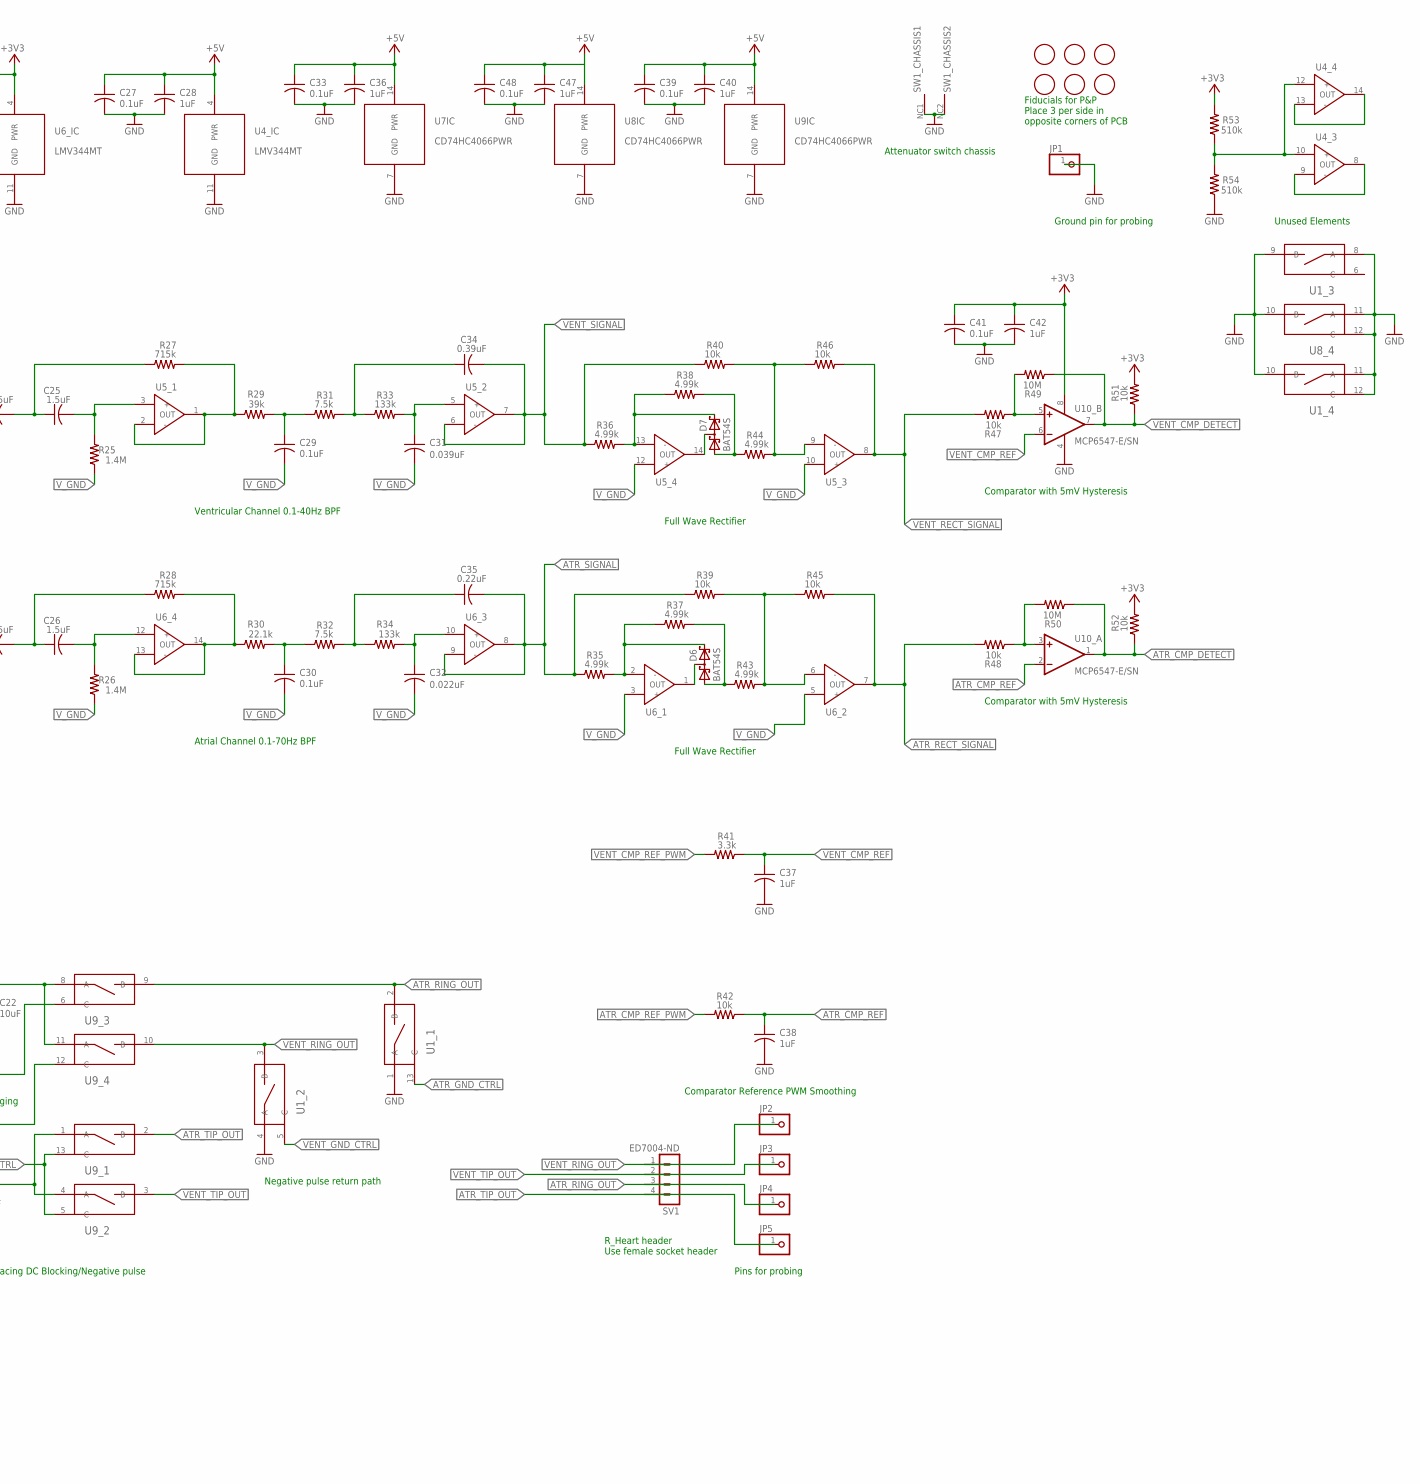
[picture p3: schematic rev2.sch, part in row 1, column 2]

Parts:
A_IA_TP: TPSTP06R; TP06R
C1, C3, C6, C14, C17, C27, C29, C30, C33, C39, C41, C43, C46, C48: 0.1uF; C0805
C2, C4, C5, C7, C8, C9, C15, C16, C20, C28, C36, C37, C38, C40, C42, C44, C45, C47: 1uF; C0805
C10, C11, C12, C13, C18, C19, C21, C22: 10uF; C0805
C23, C24, C25, C26: 1.5uF; C0805
C31: 0.039uF; C0805
C32: 0.022uF; C0805
C34: 0.39uF; C0805
C35: 0.22uF; C0805
D3, D4, D6, D7: BAT54S; SOT23
D5: BZX84C3V3LT1G; SOT23
IC1, IC2: AD623R; SO8
JP1, JP2, JP3, JP4, JP5: PINHD-1X1; 1X01
R1, R2, R3, R4, R55: 59; R0805
R5, R6: 1M; R0805
R7, R9: 100k; R0805
R8, R10: 1k; R0805
R11: 5.49k; R0805
R12, R41: 3.3k; R0805
R13, R14, R15, R16, R39, R40, R42, R45, R46, R47, R48, R51, R52: 10k; R0805
R17, R18, R21, R22: 249k; R0805
R19, R20: 1.02k; R0805
R23, R24: 330k; R0805
R25, R26: 1.4M; R0805
R27, R28: 715k; R0805
R29: 39k; R0805
R30: 22.1k; R0805
R31, R32: 7.5k; R0805
R33, R34: 133k; R0805
R35, R36, R37, R38, R43, R44: 4.99k; R0805
R49, R50: 10M; R0805
R53, R54: 510k; R0805
SV1: ED7004-ND; MA04-1
SW1: EG4208; EG4208-PACKAGE
U1, U7, U8, U9: CD74HC4066PWR; SOP65P640X110-14N
U2: ARDUINOR3-DIMENSION; ARDUINOR3
U3: TLE2426CDR; SOIC127P600X175-8N
U4, U5, U6: LMV344MT; SOP65P640X110-14N
U10: MCP6547-E/SN; SOIC127P600X175-8N
U$1, U$2, U$3, U$4, U$5, U$6: FIDUCIAL; FIDUCIAL_1MM
V_IA_TP: TPSTP06R; TP06R
X1: TSW-104-02-S-Q

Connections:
+3V3: C3.1, C4.1, C14.1, C16.1, C17.1, C20.1, C41.1, C42.1, C43.1, C44.1, D3.2 (C2), D4.2 (C2), IC1.7 (+V), IC2.7 (+V), R51.2, R52.2, R53.2, U2.3V, U3.3 (IN), U5.4 (PWR), U6.4 (PWR), U10.8 (V+)
+5V: C1.1, C2.1, C27.1, C28.1, C33.1, C36.1, C39.1, C40.1, C47.1, C48.1, U1.14 (PWR), U2.5V, U4.4 (PWR), U7.14 (PWR), U8.14 (PWR), U9.14 (PWR)
ATR_CMP_DETECT: R50.1, R52.1, U2.D0, U10.1 (OUT)
ATR_CMP_REF: C38.1, R42.1, U10.2 (-IN)
ATR_CMP_REF_PWM: R42.2, U2.D4
ATR_GND_CTRL: U1.13 (C), U2.D11
ATR_PACE_CTRL: U2.D8, U9.6 (C)
ATR_RECT_SIGNAL: R45.2, R48.2, U2.A3, U6.7 (OUT)
ATR_RING: D4.3 (C1A2), R3.2, R6.2, U7.1 (A)
ATR_RING_OUT: JP4.1, SV1.3, U1.2 (B), U8.3 (B), U9.9 (B)
ATR_SIGNAL: C35.2, R35.1, R39.1, U2.A0, U6.8 (OUT), U6.9 (-)
ATR_TIP_OUT: JP5.1, SV1.4, U9.2 (B)
FRONTEND_CTRL: U2.D13, U7.5 (C), U7.6 (C), U7.12 (C), U7.13 (C)
GND: C1.2, C2.2, C3.2, C4.2, C5.2, C6.2, C7.2, C9.1, C14.2, C15.2, C16.2, C17.2, C20.2, C21.2, C22.2, C27.2, C28.2, C33.2, C36.2, C37.2, C38.2, C39.2, C40.2, C41.2, C42.2, C45.2, C46.2, C47.2, C48.2, D3.1 (A1), D4.1 (A1), D5.1 (A), IC1.4 (-V), IC2.4 (-V), JP1.1, R2.2, R4.2, R5.1, R6.1, R11.1, R54.1, SW1.NC1 (V-), SW1.NC2 (V-), U1.1 (A), U1.4 (A), U1.7 (GND), U1.8 (A), U1.9 (B), U1.10 (B), U1.11 (A), U1.12 (C), U2.GND, U2.GND1, U2.GND2, U3.2 (COM), U4.11 (GND), U5.11 (GND), U6.11 (GND), U7.4 (A), U7.7 (GND), U7.11 (A), U8.7 (GND), U8.10 (B), U8.11 (A), U8.12 (C), U9.7 (GND), U10.4 (V-)
unnamed: C10.2, IC1.3 (+), R13.2
unnamed: C11.2, IC1.2 (-), R14.1
unnamed: C18.1, IC1.6 (OUT), V_IA_TP.TP
unnamed: IC1.1 (RG), R19.1
unnamed: R7.2, SW1.7 (A)
unnamed: C18.2, C23.1, R23.2
unnamed: C23.2, C25.1, R27.1
unnamed: C11.1, R8.1, U7.10 (B)
unnamed: C13.2, IC2.2 (-), R16.1
unnamed: C29.1, R29.2, R31.1
unnamed: C34.1, R31.2, R33.1
unnamed: C13.1, R10.1, U7.3 (B)
unnamed: D6.2 (C2), R35.2, R37.1, U6.2 (-)
unnamed: R9.2, SW1.10 (A)
unnamed: IC2.1 (RG), R20.1
unnamed: IC2.8 (RG), R20.2
unnamed: C19.2, C24.1, R24.2
unnamed: D6.3 (C1A2), U6.1 (OUT)
unnamed: IC1.8 (RG), R19.2
unnamed: C12.2, IC2.3 (+), R15.2
unnamed: C15.1, R12.1, U8.1 (A)
unnamed: C21.1, U9.1 (A), U9.4 (A)
unnamed: R22.1, R55.2, U4.1 (OUT)
unnamed: D7.3 (C1A2), U5.14 (OUT)
unnamed: R28.2, R30.1, U6.13 (-), U6.14 (OUT)
unnamed: SW1.6 (B), SW1.12 (B)
unnamed: C24.2, C26.1, R28.1
unnamed: C22.1, U8.2 (B), U9.8 (A), U9.11 (A)
unnamed: C25.2, R25.2, U5.3 (+)
unnamed: R27.2, R29.1, U5.1 (OUT), U5.2 (-)
unnamed: C5.1, U3.8 (NR)
unnamed: C31.1, R33.2, U5.5 (+)
unnamed: C30.1, R30.2, R32.1
unnamed: R48.1, R50.2, U10.3 (+IN)
unnamed: C35.1, R32.2, R34.1
unnamed: D6.1 (A1), R37.2, R43.1
unnamed: C26.2, R26.2, U6.12 (+)
unnamed: R47.1, R49.2, U10.5 (+IN)
unnamed: C32.1, R34.2, U6.10 (+)
unnamed: R39.2, R43.2, R45.1, U6.6 (-)
unnamed: SW1.3 (B), SW1.9 (B)
unnamed: C8.1, R11.2, U8.4 (A), U8.8 (A)
unnamed: A_IA_TP.TP, C19.1, IC2.6 (OUT)
unnamed: U4.8 (OUT), U4.9 (-)
unnamed: R12.2, U4.7 (OUT)
unnamed: R17.1, R21.2, U4.3 (+)
unnamed: R18.2, R22.2, U4.2 (-)
unnamed: C9.2, R18.1
unnamed: C8.2, R17.2
unnamed: U4.13 (-), U4.14 (OUT)
unnamed: R53.1, R54.2, U4.10 (+), U4.12 (+)
unnamed: R4.1, X1.7, X1.8
unnamed: R2.1, X1.3, X1.4
unnamed: R3.1, X1.5, X1.6
unnamed: R7.1, R8.2, SW1.1 (A)
unnamed: R1.1, X1.1, X1.2
unnamed: SW1.8 (COM), U7.9 (B)
unnamed: SW1.11 (COM), U7.2 (B)
unnamed: R9.1, R10.2, SW1.4 (A)
unnamed: D7.2 (C2), R36.2, R38.1, U5.13 (-)
unnamed: C12.1, SW1.5 (COM)
unnamed: C10.1, SW1.2 (COM)
unnamed: D7.1 (A1), R38.2, R44.1
unnamed: R40.2, R44.2, R46.1, U5.9 (-)
PACE_CHARGE_CTRL: U2.D5, U8.13 (C)
PACE_GND_CTRL: U2.D10, U9.5 (C), U9.13 (C)
PACING_REF_PWM: U2.D2, U4.5 (+)
VENT_CMP_DETECT: R49.1, R51.1, U2.D1, U10.7 (OUT)
VENT_CMP_REF: C37.1, R41.1, U10.6 (-IN)
VENT_CMP_REF_PWM: R41.2, U2.D3
VENT_GND_CTRL: U1.5 (C), U2.D12
VENT_PACE_CTRL: U2.D9, U9.12 (C)
VENT_RECT_SIGNAL: R46.2, R47.2, U2.A4 (A4/SDA), U5.8 (OUT)
VENT_RING: D3.3 (C1A2), R1.2, R5.2, U7.8 (A)
VENT_RING_OUT: JP2.1, SV1.1, U1.3 (B), U8.9 (B), U9.10 (B)
VENT_SIGNAL: C34.2, R36.1, R40.1, U2.A1, U5.6 (-), U5.7 (OUT)
VENT_TIP_OUT: JP3.1, SV1.2, U9.3 (B)
VIN: U2.VIN
V_GND: C6.1, C7.1, C29.2, C30.2, C31.2, C32.2, C43.2, C44.2, C45.1, C46.1, IC1.5 (REF), IC2.5 (REF), R13.1, R14.2, R15.1, R16.2, R21.1, R23.1, R24.1, R25.1, R26.1, U3.1 (OUT), U4.6 (-), U5.10 (+), U5.12 (+), U6.3 (+), U6.5 (+)
Z_ATR_CTRL: U2.D6, U8.5 (C)
Z_SIGNAL: D5.3 (C), R55.1, U2.A2
Z_VENT_CTRL: U2.D7, U8.6 (C)

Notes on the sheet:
Ventricular Channel 0.1-40Hz BPF
Atrial Channel 0.1-70Hz BPF
Pacing Charging and Discharging
Unused Elements
Lead Impedance Measurement Amp
Pacing DC Blocking/Negative pulse
Comparator with 5mV Hysteresis
Comparator Reference PWM Smoothing
Footprint only Populate with 0.1" headers
Differential Amplifier, G=10
3.3V to 5V PWM converter
Input ground referencing and protection
Switchable x1/x100 Input Attenuator
R_Heart header Use female socket header
Negative pulse return path
Full Wave Rectifier
Virtual Ground
Distributed decoupling Place far from U3
Input Connections Use MOLEX 0397000204/Phoenix 1705003 or similar Spring Terminal Block
Pins for probing
Fiducials for P&P Place 3 per side in opposite corners of PCB
Ground pin for probing
Attenuator switch chassis
3.3V Zener clamp

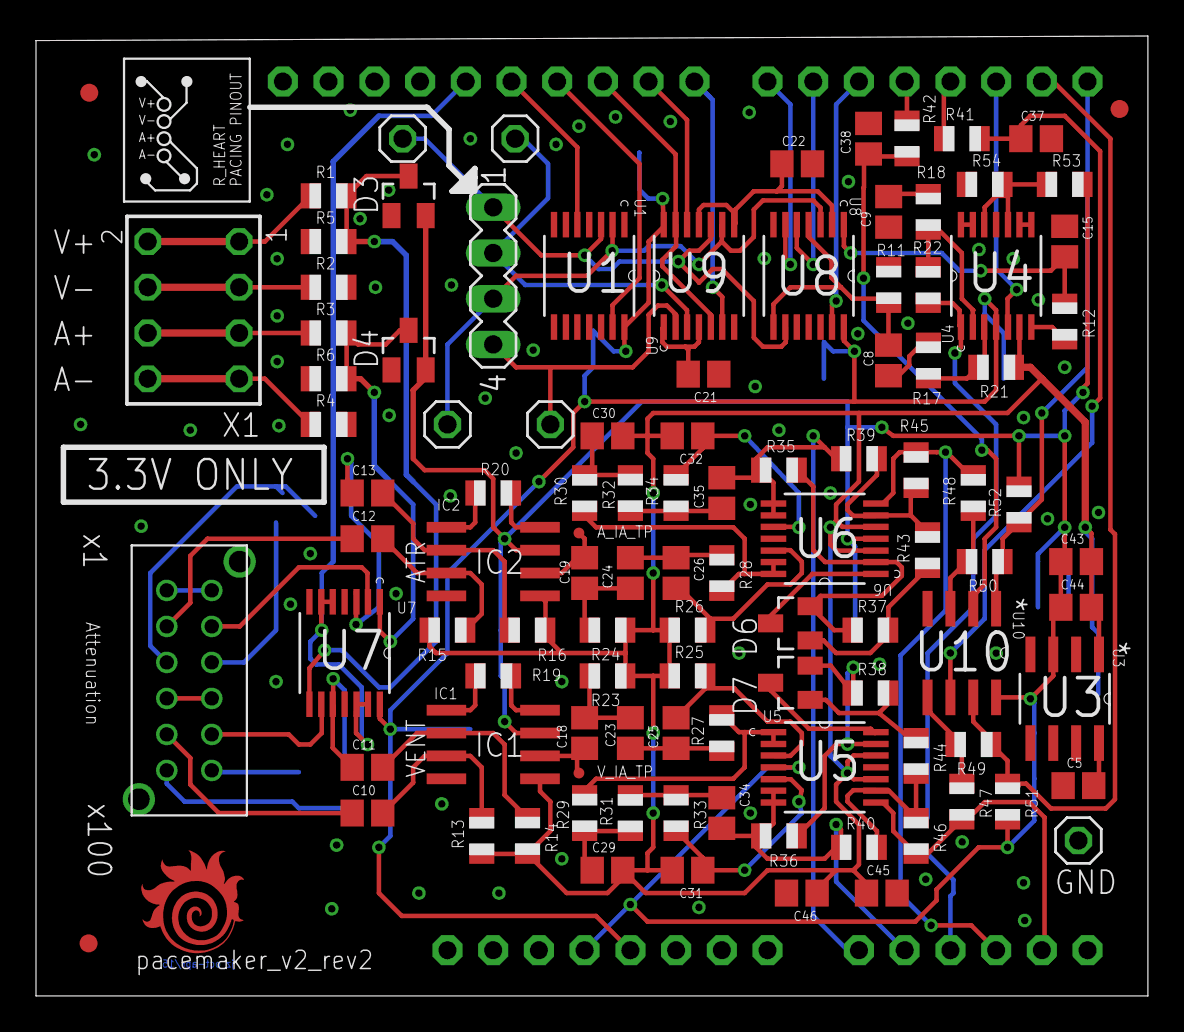
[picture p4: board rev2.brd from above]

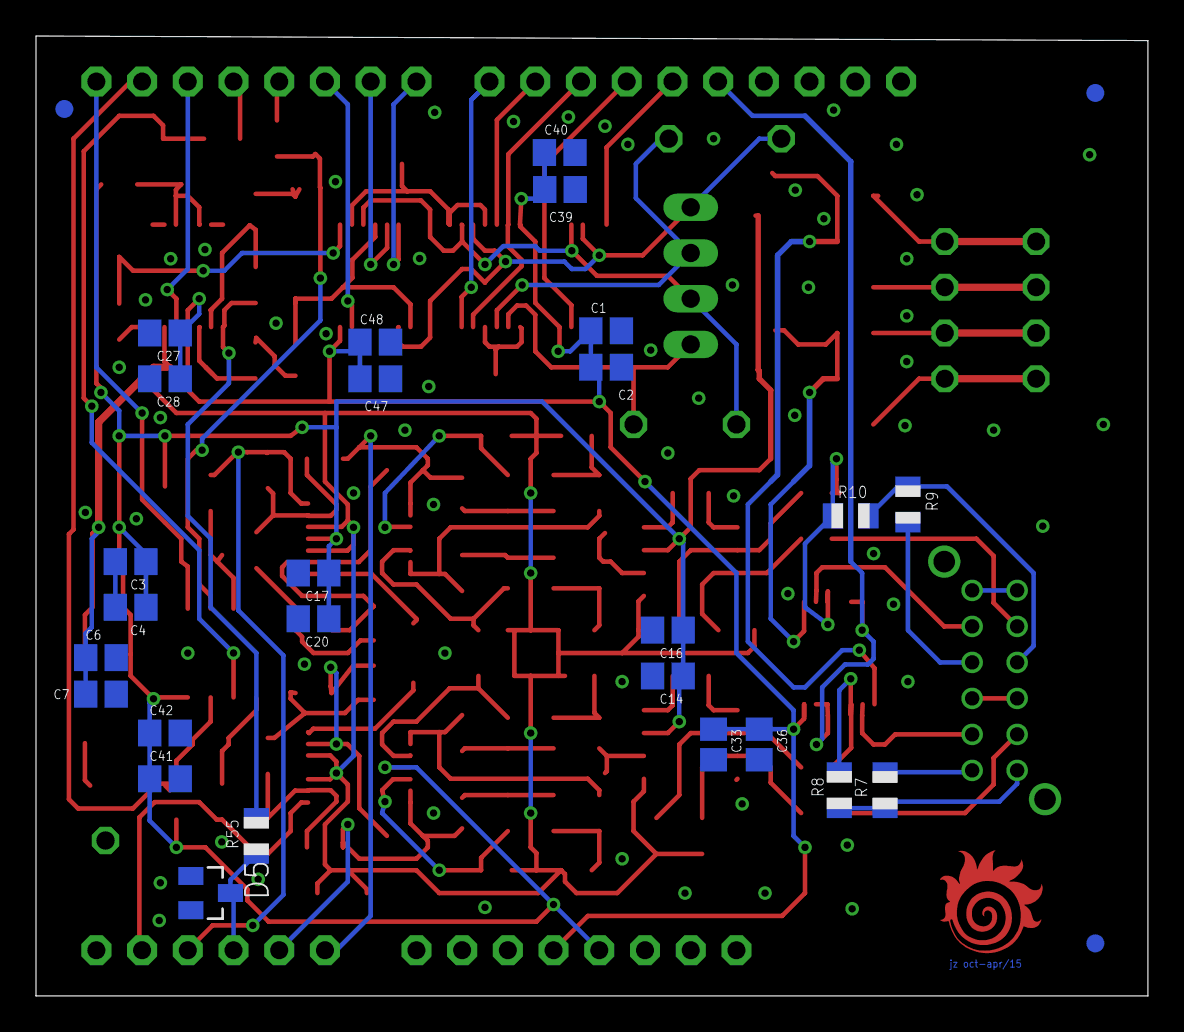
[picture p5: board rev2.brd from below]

Board: 2 copper layers, 61.8 x 53.3 mm, 137 parts (29 on the bottom side), 95 nets.

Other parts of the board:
U$7: FIREBALL

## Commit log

2020-07-20 add shields files
    [BOM_SHIELD_B_REV0.csv, Board B RevA BOM.xlsx, Board B RevA STEP model .step, Board B RevA STEP model June 29.step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]
2020-07-20 mechanical casing
    [casing_bottom_drawing_only_1to1.dwg, casing_bottom_drawing_only_1to1.dxf, casing_top_drawing_only_1to1.dwg, casing_top_drawing_only_1to1.dxf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]
2020-07-20 updated BOM nucleo
    [BOM_Heart_RevA.xlsx, shield_B_heart_BOM.xlsx]
2020-07-21 updated BOM
    [BOM_Heart_RevA.xlsx, BOM_Pacemaker_REV3.xlsx]
2020-07-31 fix plots to 5V
2020-08-28 update pcb design
    [BOM_Heart_RevA.xlsx, BOM_Pacemaker_REV3.xlsx, Pace Maker Panel RevA.DRL, Pace Maker Panel RevA.GBL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]
2020-08-28 connector spec
2020-09-08 add shield fab docs
    [Pacemaker Rev3_0.PrjPcb, Pacemaker V3_0.SchDoc, pacemakerv3_0.PcbDoc]
